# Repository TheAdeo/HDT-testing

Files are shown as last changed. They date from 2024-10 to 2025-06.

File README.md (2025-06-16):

# DIY HDT Testing Standard v3.1
## Introduction
This is an attempt at creating an easy to follow procedure for an easy and DIY standardised HDT testing of 3D printing polymers, taking inspiration from the ISO 75 methods.

Considering the difficulties of actually making something easily reproducible by anyone with a 3D printer and a PID tuned oven, I have drafted the parameters of the test to make it simpler than the ISO 75 standard, losing some accuracy in the process and making the results of the two not directly comparable (but still close).
This accuracy loss is not a problem as traditional ISO 75 tests require injection molded samples, as with FDM 3D printed samples too many parameters, some of which are not controllable, can influence the results.

Two load cases are suggested, to try and match the HDT/A and HDT/B values commonly found on 3D printer filaments technical datasheets.

A big difference compared to the ISO 75 test is that the temperature ramp is four times as slow, to allow time for the sample to deform and get a number that's more true to real life compared to a faster test that always overestimates the result.

<!-------------------------------------------------------------------------------------------------->
</br>

---

## Testing Methodology
### • Brief Description
A printed sample in the shape of a bridge is put inside a temperature controlled oven and slowly heat up. As soon as the deformation is enough for the bridge to touch a fixed height gauge the test is over and the last temperature value at the fail instant is assumed to be the test result.

### • Printing Parameters
The test sample shall be printed with the flat rectangular reference face laying downwards on the build plate. <br />
The test sample shall be scaled to account for material shrinkage during the printing process, so that the top reference surface of the bridge is within the following dimensions:

| Dimension  | Value (mm) |
| :--------- | :--------: |
| Length     | 140 ±0.2   |
| Width      | 20 ±0.2    |
| Thickness  | 2 ±0.1     |

The test object shall be printed with a 0.4mm/0.5mm nozzle, and the following settings have to be used in the slicer:

| Setting              | Value               |
| :----------          | :----------:        |
| Line Width           | 0.65mm              |
| Layer Height         | 0.2mm               |
| N° of Perimeters     | 4                   |
| N° of Top Layers     | 0                   |
| N° of Bottom Layers  | 0                   |
| Infill %             | 100%                |
| Infill Type          | Aligned Rectilinear |
| Infill Angle         | 0°                  |
| Print Speed          | 30mm/s              |
| Extrusion Multiplier | 1.05                |

Both the Classic and Arachne slicing engines are allowed. <br />

The height gauge can be printed with any slicer parameters, as long as it's made out of the same material as the test sample or out of a material with better thermal properties.

These settings have been chosen to get maximum possible strength to the sample and maximize compatibility, and have been fixed to remove variability in the results. <br />
The three parameters that have been left to be changed depending on the material are _Hotend Temperature_, _Chamber Temperature_ and _Cooling Fan Percentage_. <br />
It is reccommended to note them and add them near the test results to make them valid and reproducible. <br />

Before printing it has to be verified that when requesting 100mm of extrusion, 100mm of filament are extruded. If not an e-steps calibration must be performed. <br />
The filament diameter must be measured with a caliper and set correctly in the slicer.

### • Test A - 1.8MPa (similar to HDT/A) - RECOMMENDED TEST
The test sample shall be loaded with 4 standard ISO 4032 or DIN 934 M12 steel nuts (17.3g each), making sure they are stacked on top of each other securely and located in the middle of the bridge (marked with lines on the underside).

### • Test B - 0.45MPa (similar to HDT/B) - DEPRECATED, DO NOT USE
~The test sample shall be loaded with 1 standard ISO 4032 or DIN 934 M12 steel nuts (17.3g), making sure it is located in the middle of the bridge (marked with lines on the underside).~

### • Height Gauge Setup
The height gauge requires a M3x5x4mm or M3x5x5mm threaded insert, installed from the top side. <br />
After loading the bridge with the nuts, a M3x8 screw (SHCS or hex bolt recommended) on the height gauge shall be fixed at 1mm below the bottom surface of the bridge by tightening a M3 nut (that acts as a jam nut) against the M3 threaded insert. The 1mm could be measured with calipers subtracting the height of the gauge from the height of the loaded bridge, or by using a 1±0.1mm shim. <br />
Different setups are allowed, as long as they can be tuned so that the fail criteria is 1mm of additional deformation after the test start.

<picture>
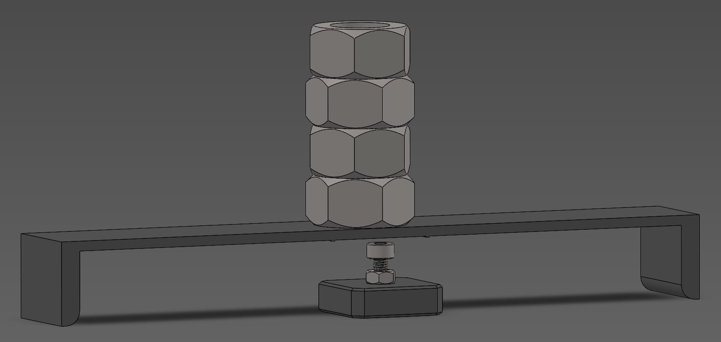
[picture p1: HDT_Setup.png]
Test setup image
  
</picture>

### • Shielding
The test objects should be shielded with some aluminium foil from radiant sources of heat of the oven, by making a foil barrier between the emitting source and the object.

### • Temperature Rise
The oven shall be set with a ramp starting from 25°C rising 0.5°C/min, to make sure the sample can stabilize at the oven temperature and to give time for the sample to flex when it reaches the softening point corresponding to the specified test. <br />
The test stops when the sample flexes enough to touch the height gauge, or when 1mm of additional deformation is measured.

### • Results
The results shall be distributed by specifying which load was used, the test version (currently v3.0), and what were the _Hotend Temperature_, _Chamber Temperature_ and _Cooling Fan Percentage_ used for printing the sample.
The temperature chosen as the test result is the last temperature recorded at the end of the test, rounded to the nearest integer.
Multiple samples are highly suggested, in that case the result is the arithmetic average of the individual results, rounded to the nearest integer.

<!-------------------------------------------------------------------------------------------------->
</br>

---

## Automation
The deflection identification can be automated to allow for zero supervision tests. This requires adding some aluminum tape to the bottom of the bridge, and attaching one wire to the tape and one wire to the screw of the height gauge. The wires can be attached to something that detects the closing of the circuit, like a LED or an Arduino, so that when the circuit is completed the temperature is recorded as the result and the test ends.

<!-------------------------------------------------------------------------------------------------->
</br>

---

## Calculation of the stresses in each test case
In this section I'll add the calculations that led me to choose the size and loads to match the ISO 75 standard.

<!-------------------------------------------------------------------------------------------------->
</br>

---

## Comments
I have to add the calculations that led me to these parameters.
I have to explain a way to automate the test, to remove the human factor entirely.
You can also download the model on Printables for free to support me (not updated to v3.0 yet, still v2.0 files):

https://www.printables.com/model/1055576-heat-deflection-temperature-hdt-tester-v2

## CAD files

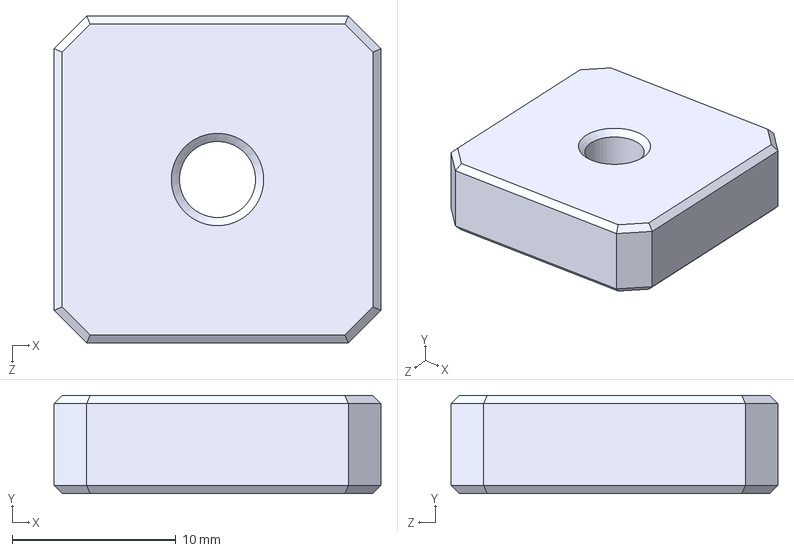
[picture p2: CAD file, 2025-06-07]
DIY Height Gauge.STEP
20.0 x 6.00 x 20.0 mm

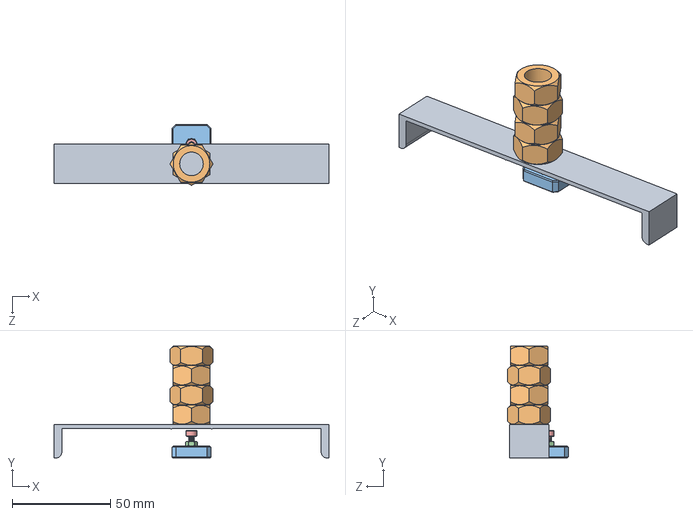
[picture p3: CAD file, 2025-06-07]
HDT TEST DIY.STEP
140.0 x 57.0 x 31.0 mm
HDT Sample DIY
DIY Height Gauge

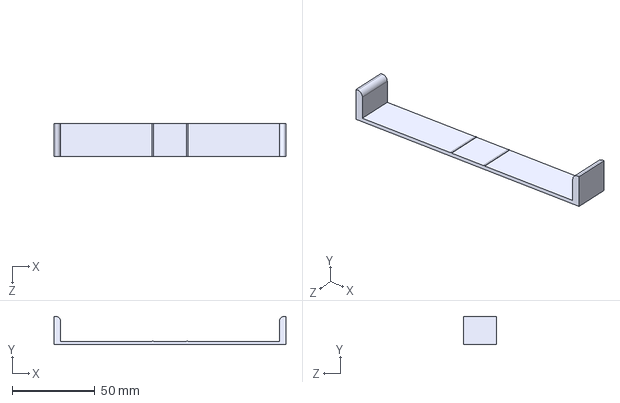
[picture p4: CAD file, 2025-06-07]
HDT Sample DIY.STEP
140.0 x 17.0 x 20.0 mm

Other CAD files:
DIY Height Gauge.STL
HDT Sample DIY.STL

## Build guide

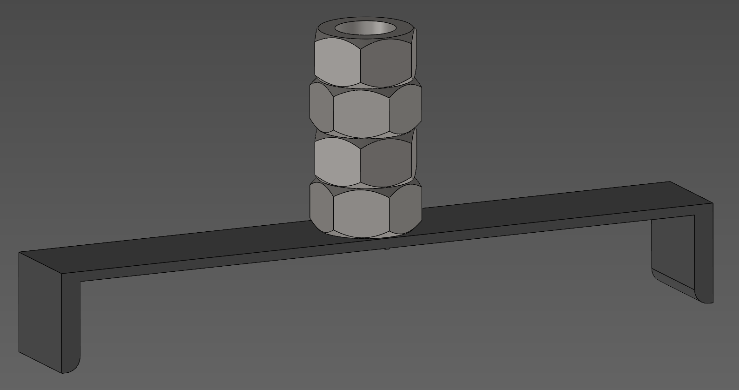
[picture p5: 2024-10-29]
HDT Setup.png

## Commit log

2024-05-08 Specified printing orientation
2024-05-08 Added Printables link
2024-05-08 Changed the bridge legs
    [HDT Bridge.STEP, HDT Bridge.STL]
2024-05-08 Re added files
    [HDT Bridge.STL, HDT Pillar.STL, HDT Sample.STEP]
2024-10-29 Removed pillar
    [HDT Sample.STEP, HDT Sample.STL]
2024-10-29 Rotated the sample for the correct printing orientation
    [HDT Sample.STL]
2024-10-29 Update printables link
2025-06-07 Added files for v3.0
    [DIY Height Gauge.STEP, DIY Height Gauge.STL, HDT Sample DIY.STEP, HDT Sample DIY.STL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]
2025-06-07 Explained threaded insert
